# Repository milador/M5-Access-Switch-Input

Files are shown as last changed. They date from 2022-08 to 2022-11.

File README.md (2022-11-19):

# M5-Access-Switch-Input

A Bluetooth enabled Adaptive Switch Interface based on ESP32 M5StickC/M5StickCPlus, and the Switch Input module which offers up to two 3.5mm switch inputs. 

The Adaptive Switch Interface includes 4 operating modes: 

    1. Switch Mode
    2. Switch Mac Mode  
    3. Morse Keyboard Mode 
    4. Media Control Mode
    5. Settings Mode
	
The mode can be changed by pressing and holding Switch A for 4 seconds or pressing M5 button.

<p align="center">
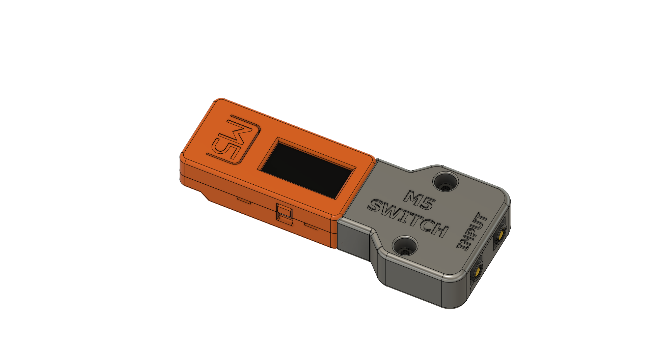
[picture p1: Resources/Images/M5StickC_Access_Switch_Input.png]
M5StickC_Access_Switch_Input

</p>

## Requirements and setup instructions 
The setup process is divided to three main catagories:

  1. [Hardware](./Hardware/) : The required hardware and design files
  2. [Software](./Software/) : The required software
  3. [Documentation](./Documentation/) : The assembly guide,user guide and other documents 

## License

### MIT License

Copyright (c) 2022 milador

Permission is hereby granted, free of charge, to any person obtaining a copy of this software and associated documentation files (the "Software"), to deal in the Software without restriction, including without limitation the rights to use, copy, modify, merge, publish, distribute, sublicense, and/or sell copies of the Software, and to permit persons to whom the Software is furnished to do so, subject to the following conditions:

The above copyright notice and this permission notice shall be included in all copies or substantial portions of the Software.

THE SOFTWARE IS PROVIDED "AS IS", WITHOUT WARRANTY OF ANY KIND, EXPRESS OR IMPLIED, INCLUDING BUT NOT LIMITED TO THE WARRANTIES OF MERCHANTABILITY, FITNESS FOR A PARTICULAR PURPOSE AND NONINFRINGEMENT. IN NO EVENT SHALL THE AUTHORS OR COPYRIGHT HOLDERS BE LIABLE FOR ANY CLAIM, DAMAGES OR OTHER LIABILITY, WHETHER IN AN ACTION OF CONTRACT, TORT OR OTHERWISE, ARISING FROM, OUT OF OR IN CONNECTION WITH THE SOFTWARE OR THE USE OR OTHER DEALINGS IN THE SOFTWARE.

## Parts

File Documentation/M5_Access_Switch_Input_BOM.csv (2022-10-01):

Index | Quantity | Component | Digikey Part Number | Manufacturer Part Number | Description | Unit Price (CAD) | Price (CAD) | Link
1 | 1 |  | 2221-K016-P-ND | K016-P | M5STICKC PLUS ESP32-PICO IOT KIT | 31.48 | 31.48 | https://www.digikey.ca/en/products/detail/m5stack-technology-co-ltd/K016-P/13148797
2 | 2 | SW1,SW2 | CP-43514-ND | SJ-43514 | CONN JACK 4COND 3.5MM | 1.48 | 2.96 | https://www.digikey.ca/en/products/detail/SJ-43514/CP-43514-ND/368146
3 | 2 | OK1,OK2 | 160-1366-5-ND | LTV-817 | OPTOISOLATR 5KV TRANSISTOR 4-DIP | 0.58 | 1.16 | https://www.digikey.ca/en/products/detail/liteon/LTV-817/385836
4 | 1 | JP1 | 609-3321-ND | 68016-208HLF | CONN HEADER R/A 8POS 2.54MM | 0.7 | 0.7 | https://www.digikey.ca/en/products/detail/amphenol-cs-fci/68016-208HLF/1878499
5 | 2 | R1,R2 | S1KQCT-ND | CFM14JT1K00 | RES 1K OHM 5% 1/4W AXIAL | 0.15 | 0.3 | https://www.digikey.ca/en/products/detail/stackpole-electronics-inc/CFM14JT1K00/1742111
6 | 2 | R3,R4 | 738-CFM14JA470RCT-ND | CFM14JA470R | RES 470 OHM 5% 1/4W AXIAL | 0.15 | 0.3 | https://www.digikey.ca/en/products/detail/stackpole-electronics-inc/CFM14JA470R/1742225
7 | 2 | N/A | 145-50M025045P006-ND | 50M025045P006 | PAN PHILLIPS SCREW, M2.5 X 4.5 T | 0.23 | 0.46 | https://www.digikey.ca/en/products/detail/essentra-components/50M025045P006/11638590
8 | 2 | N/A | 36-9600-ND | 9600 | HEX NUT 1/4" STEEL 4-40 | 0.16 | 0.32 | https://www.digikey.ca/en/products/detail/keystone-electronics/9600/2746248
 |  |  |  |  |  | Total Price (CAD) | 37.68

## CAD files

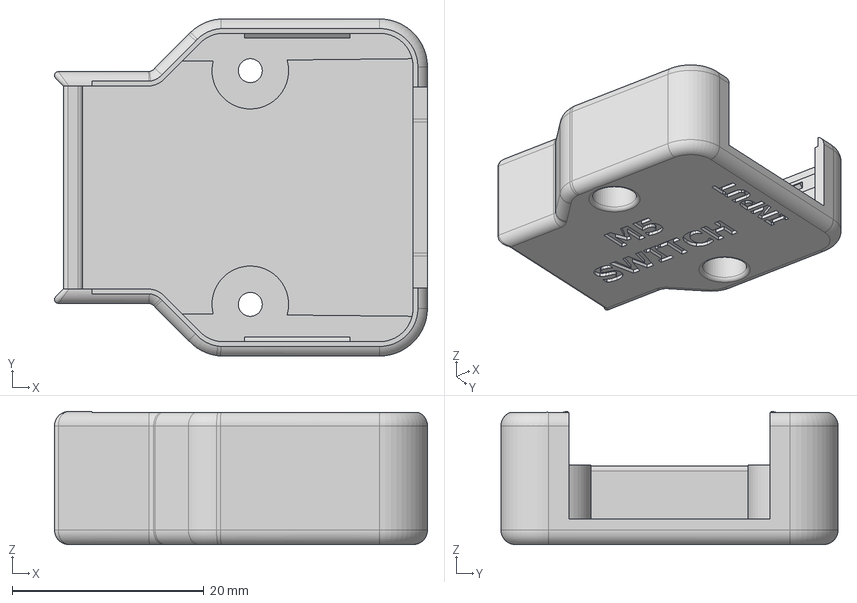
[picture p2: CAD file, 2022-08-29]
Hardware/Case/STEP/M5StickC_Switch_Input_Main.step
38.9 x 35.2 x 13.9 mm

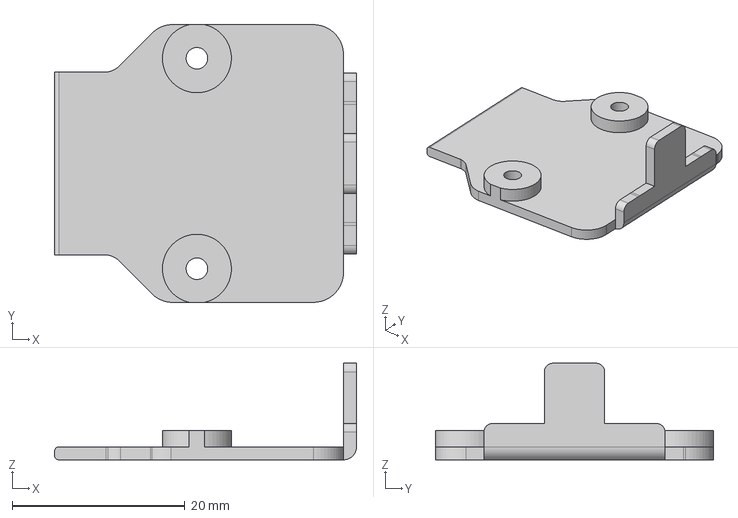
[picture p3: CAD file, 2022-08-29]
Hardware/Case/STEP/M5StickC_Switch_Input_Bottom.step
35.0 x 32.2 x 11.2 mm

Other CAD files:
Hardware/Case/STL/M5StickC_Switch_Input_Bottom.stl
Hardware/Case/STL/M5StickC_Switch_Input_Main.stl

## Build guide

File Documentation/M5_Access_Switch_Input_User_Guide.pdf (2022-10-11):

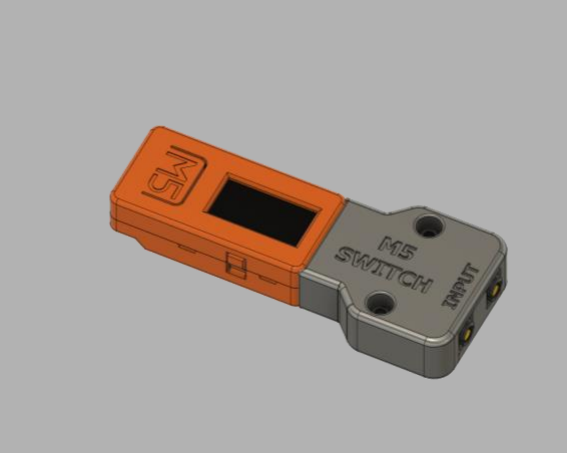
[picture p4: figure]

# M5 ACCESS SWITCH INPUT USER GUIDE (V1.0)

A wireless switch interface device

Milad Hajihassan
https://github.com/milador/M5-Access-Switch-Input

1

## Contents

Usage requirements | 2
Usage Components | 2
Usage Process | 2
How to Use? | 2
How to Customize? | 2
Sleep Mode | 3

2

## Usage requirements

Usage Components

1. Adaptive Switch x 2 ( Example: AJelly Bean (https://www.ablenetinc.com/jelly-bean) )

## Usage Process

How to Use?

1. Connect two Adaptive Switches to the Switch Input module through 3.5mm switch connectors.
1.1. Switch A
1.2. Switch B
2. Connect and pair to the host device (Example: Windows 10 PC)

On Windows 10:

2.1. Select Start > Settings > Devices > Bluetooth & other devices 2.2. Select Add Bluetooth or other device > Bluetooth. 2.3. Choose Qwiic BLE Switch and follow additional instructions if they appear. 2.4. Select Done once the device is paired.
3. Switch between modes by press and holding Switch A for 4 seconds or by pressing M5 button.
3.1. Switch Mode: Windows and Android, Switch A : a Key, Switch B : b Key
3.2. Switch Mac Mode: Mac, Switch A : F1 Key, Switch B : F2 Key
3.3. Morse Keyboard Mode: Switch A : Dot, Switch B : Dash
3.4. Media Control Mode: Switch A : Previous Track, Switch B : Next Track
3.5. Settings Mode: Change reaction time, Switch A : Decrease Reaction level, Switch B : Increase Reaction level

How to Customize?

1. Enter Settings Mode by press holding switch A 3 times for 4 seconds or by pressing M5

button. The screen will display a text in yellow to indicate it's in Settings Mode.

3

2. Press Switch A to Decrease Reaction level ( Maximum is 1 ) : 500ms
3. Press Switch B to Increase Reaction level ( Minimum is 10 ) : 50ms

Sleep Mode

The device goes to sleep mode if it’s not used for more than one minute and automatically wakes up every 3 minutes. The device can be woken up if switch A or Switch B is pressed when the device is in sleep mode.

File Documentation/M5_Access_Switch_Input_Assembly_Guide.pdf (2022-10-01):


# M5 ACCESS SWITCH INPUT ASSEMBLY GUIDE (V1.0)

A wireless switch interface device

### Milad Hajihassan

https://github.com/milador/M5-Access-Switch-Input

1

## Contents

Components List | 2
Software | 3
Installing Arduino IDE | 3
Installing Arduino Libraries | 3
Board Support Packages | 3
Required Software and libraries | 3
Uploading Software | 5
Hardware Assembly | 6
Enclosure design | 6
M5 Access Switch Input Assembly | 7

2

## Components List

1. M5STICKC PLUS ESP32-PICO IOT KIT x 1
2. SJ-43514 3.5MM TRRS AUDIO JACK x 2
3. LTV-817 OPTOISOLATR x 2
4. 8 POSITION MALE RIGHT ANGLE HEADER x 1
5. 1K OHM 1/4W RESISTOR x 2
6. 470 OHM 1/4W RESISTOR x 2
7. M2.5 SCREW (8MM) x 2
8. M2.5 SCREW NUT x 2

The bill of materials can also be downloaded from GitHub repository under main directory.

https://github.com/milador/M5-Access-Switch-

Input/blob/main/Documentation/M5_Access_Switch_Input_BOM.csv (https://github.com/milador/M5-Access-Switch-Input/blob/main/Documentation/M5_Access_Switch_Input_BOM.csv)

3

## Software

The Switch Input software can be downloaded from the GitHub repository under software directory.

https://raw.githubusercontent.com/milador/M5-Access-Switch-Input/develop/Software/M5_Access_Switch_Input_Software/M5_Access_Switch_Input_Software.ino (https://raw.githubusercontent.com/milador/M5-Access-Switch-Input/main/Software/M5_Access_Switch_Input_Software/M5_Access_Switch_Input_Software.ino)

### Installing Arduino IDE

The Arduino IDE is required to compile and upload the source code to the MCU in your M5StickC device. You can download and install the Arduino from official Arduino website that you can find using following link:

https://www.arduino.cc/en/software

### Installing Arduino Libraries

The following instructions on how to install additional Arduino libraries helps you to get started with setting up Arduino IDE with required libraries and dependencies.

https://www.arduino.cc/en/guide/libraries

Board Support Packages
You can find the official instructions to install Board Support Packages on M5Stack website using following link:

https://docs.m5stack.com/en/quick_start/m5stickc/arduino

Alternatively, you can perform following instructions to install Board Support Packages:

1. Open and start the Arduino IDE.
2. Go to File > Preferences.
3. Add following link as a new line under Additional Board Manager URLs
- https://m5stack.oss-cnshenzhen.aliyuncs.com/resource/arduino/package_m5stack_index.json (https://m5stack.oss-cn-shenzhen.aliyuncs.com/resource/arduino/package_m5stack_index.json)
4. Restart the Arduino IDE
5. Open the Boards Manager option from the Tools > Board menu and install M5Stack by M5Stack official
6. Wait until the IDE finishes installing the cross-compiling toolchain and tools associated with Board Support Package. This may take few minutes.
7. That’s it! The installation of Board Support Packages is finished.

Required Software and libraries
The software requirements:
- M5_Access_Switch_Input_Software.ino (https://raw.githubusercontent.com/milador/M5-Access-Switch-Input/develop/Software/M5_Access_Switch_Input_Software/M5_Access_Switch_Input_Software.ino)
- M5StickC Plus (https://github.com/m5stack/M5StickC-Plus)
- ESP32-BLE-Keyboard (https://github.com/milador/ESP32-BLE-Keyboard)
- StopWatch Library (https://github.com/RobTillaart/Stopwatch_RT)
- EasyMorse Library (https://github.com/milador/EasyMorse)

4

Note: This project is using edited version of ESP32-BLE-Keyboard library by T-vK.

You can use the following instructions to download and install the required libraries:

1) Visit the M5StickC-Plus library github repository page.
2) Click on Code > Download Zip to download M5StickC-Plus.
3) Extract M5StickC-Plus-master.zip file
4) Rename M5StickC-Plus-master folder to M5StickC-Plus folder under M5StickC-Plus-master subdirectory.
5) Copy or move M5StickC-Plus folder to Arduino installation library subdirectory. As an example: This is found under C:\Program Files (x86)\Arduino\libraries in windows 10.
6) Visit the ESP32-BLE-Keyboard library github repository page.
7) Click on Code > Download Zip to download ESP32-BLE-Keyboard.
8) Extract ESP32-BLE-Keyboard-master.zip file
9) Rename ESP32-BLE-Keyboard-master folder to ESP32-BLE-Keyboard folder under ESP32-BLE-Keyboard-master subdirectory.
10) Copy or move ESP32-BLE-Keyboard folder to Arduino installation library subdirectory. As an example: This is found under C:\Program Files (x86)\Arduino\libraries in windows 10.
11) Visit the StopWatch library github repository page.
12) Click on Code > Download Zip to download StopWatch library.
13) Extract Stopwatch_RT-master.zip file
14) Rename Stopwatch_RT-master folder to Stopwatch folder under Stopwatch_RT-master subdirectory.
15) Copy or move Stopwatch folder to Arduino installation library subdirectory. As an example: This is found under C:\Program Files (x86)\Arduino\libraries in windows 10.
16) Visit the EasyMorse library github repository page.
17) Click on Code > Download Zip to download EasyMorse library.
18) Extract EasyMorse-master.zip file
19) Rename EasyMorse-master folder to EasyMorse folder under EasyMorse-master subdirectory.
20) Copy or move EasyMorse folder to Arduino installation library subdirectory. As an example: This is found under C:\Program Files (x86)\Arduino\libraries in windows 10.
21) Visit the M5_Access_Switch_Input_Software.ino raw source code file under Software directory.
22) Right click on the source code or any place on this page and select Save Page As…
23) Select the directory you would like to save the software in your computer.
24) Change File name from M5_Access_Switch_Input_Software to M5_Access_Switch_Input_Software.ino
25) Change Save as type to All Files.
26) Click on Save button.
27) Open the directory you selected in step 23.
28) Double left click or open M5_Access_Switch_Input_Software file
29) Arduino IDE will ask your permission to create a new sketch folder named M5_Access_Switch_Input_Software and move M5_Access_Switch_Input_Software.ino under this folder.
30) Click on the Ok button.
31) Arduino IDE should now open the M5_Access_Switch_Input_Software.ino file automatically.

5

Uploading Software
Note: Make sure all files are included in your local copy of Software directory before uploading it to the M5StickC device. The libraries can be installed in Arduino libraries.

You can go ahead and upload the downloaded M5_Access_Switch_Input_Software.ino code to M5StickC using Arduino IDE once all the necessary libraries are installed.

1. Start the Arduino IDE
2. Open M5_Access_Switch_Input_Software.ino
3. Select the Board under Tools > Board > M5Stick Arduino Boards as M5Stick-C-Plus
4. Select the correct port number under Tools > Port which should show COM XX (M5Stick-C-Plus)

Note: It’s very important to make sure the correct Board and port number are selected as selecting the wrong board may result problems with bootloader of M5StickC device.

5. Press the Verify button to make sure there is no problem with the software and libraries.
6. Press Upload button

You can now go ahead and upload the software. Arduino IDE will show you a Done Uploading message indicating the software is uploaded to your M5StickC device.

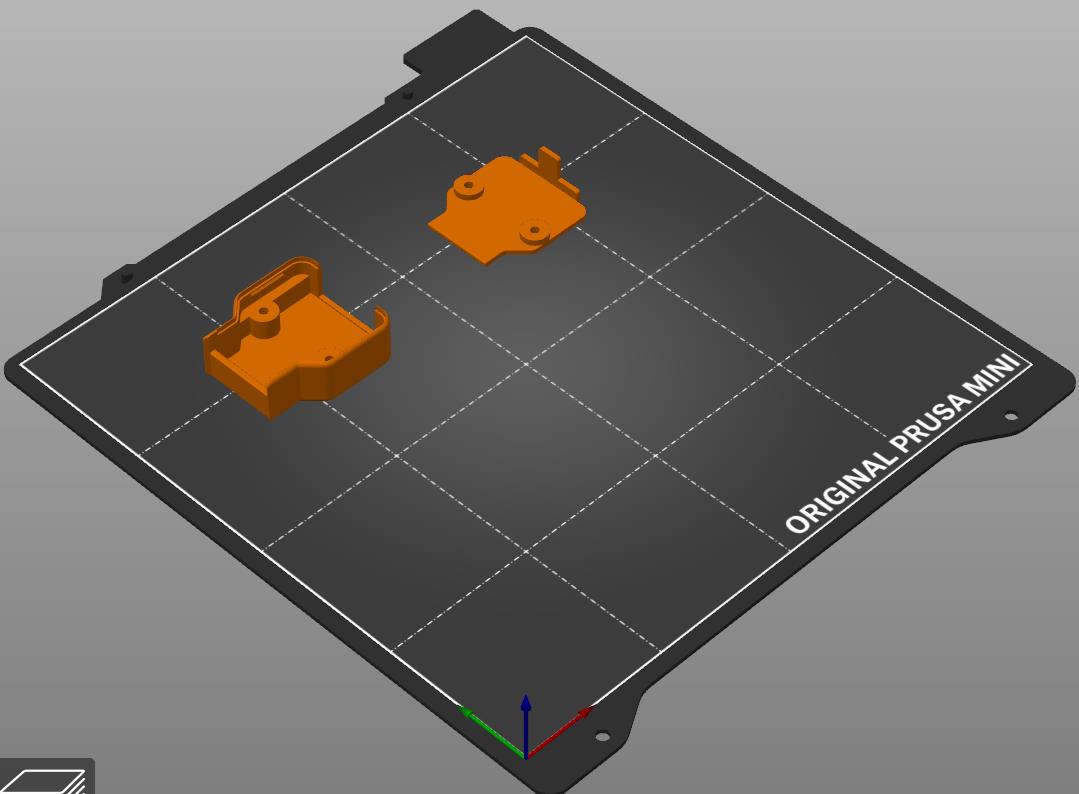
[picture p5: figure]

6

## Hardware Assembly

### Enclosure design

The enclosure/housing files in STL format can be downloaded from GitHub repository under Hardware and Case subdirectory.

- M5StickC_Switch_Input_Main.STL
- M5StickC_Switch_Input_Bottom.STL

https://github.com/milador/M5-Access-Switch-Input/tree/main/Hardware/Case/STL

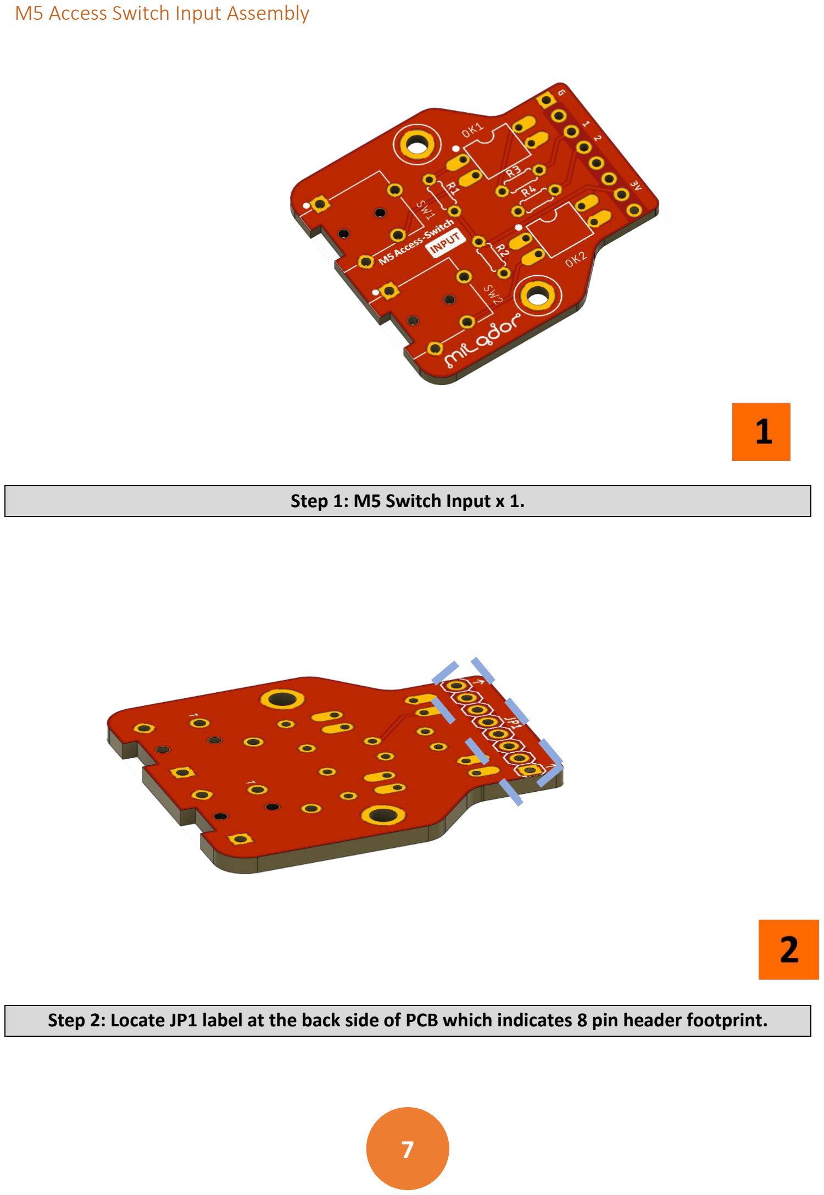
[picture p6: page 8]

7

### M5 Access Switch Input Assembly

Step 1: M5 Switch Input x 1.
Step 2: Locate JP1 label at the back side of PCB which indicates 8 pin header footprint.

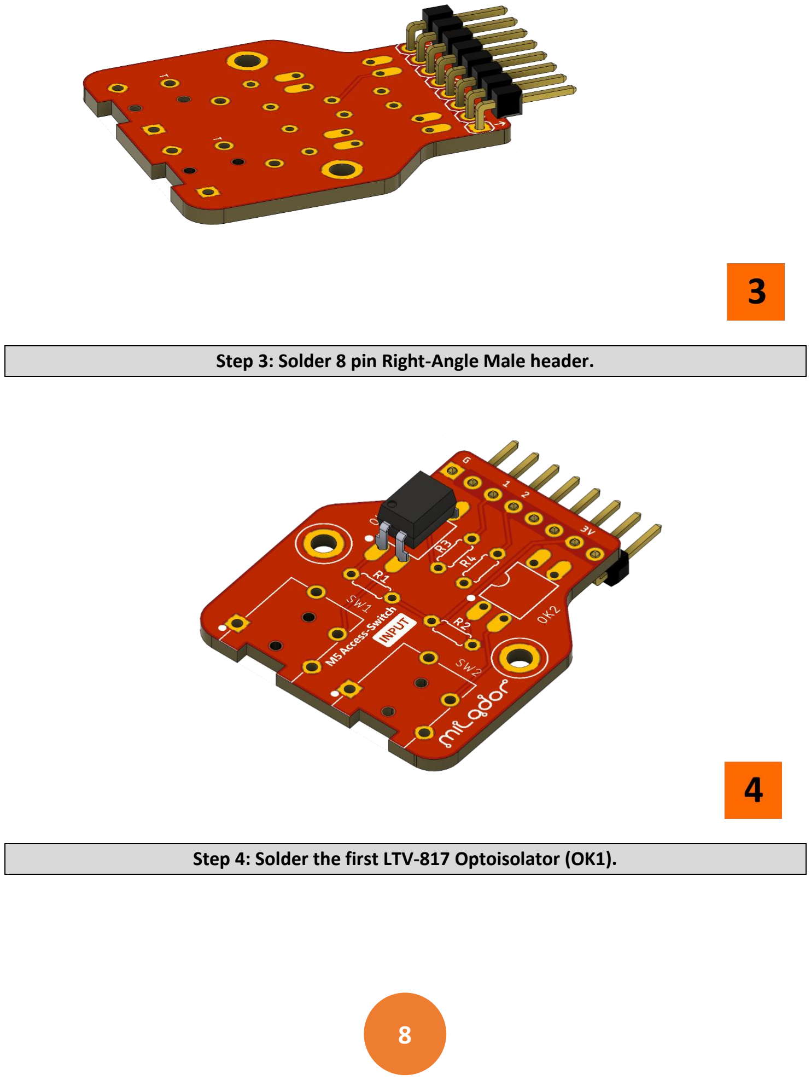
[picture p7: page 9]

8

Step 3: Solder 8 pin Right-Angle Male header.
Step 4: Solder the first LTV-817 Optoisolator (OK1).

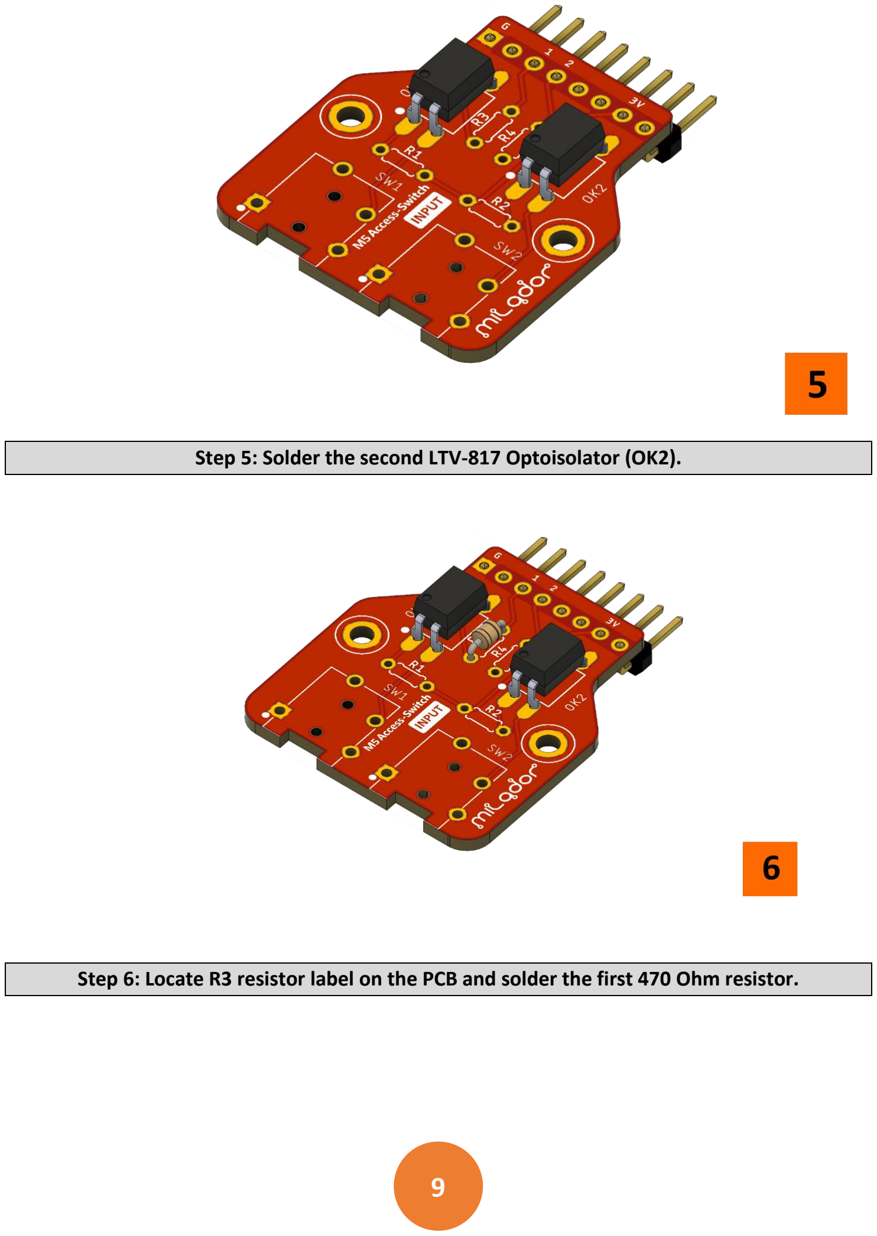
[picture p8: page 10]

9

Step 5: Solder the second LTV-817 Optoisolator (OK2).
Step 6: Locate R3 resistor label on the PCB and solder the first 470 Ohm resistor.

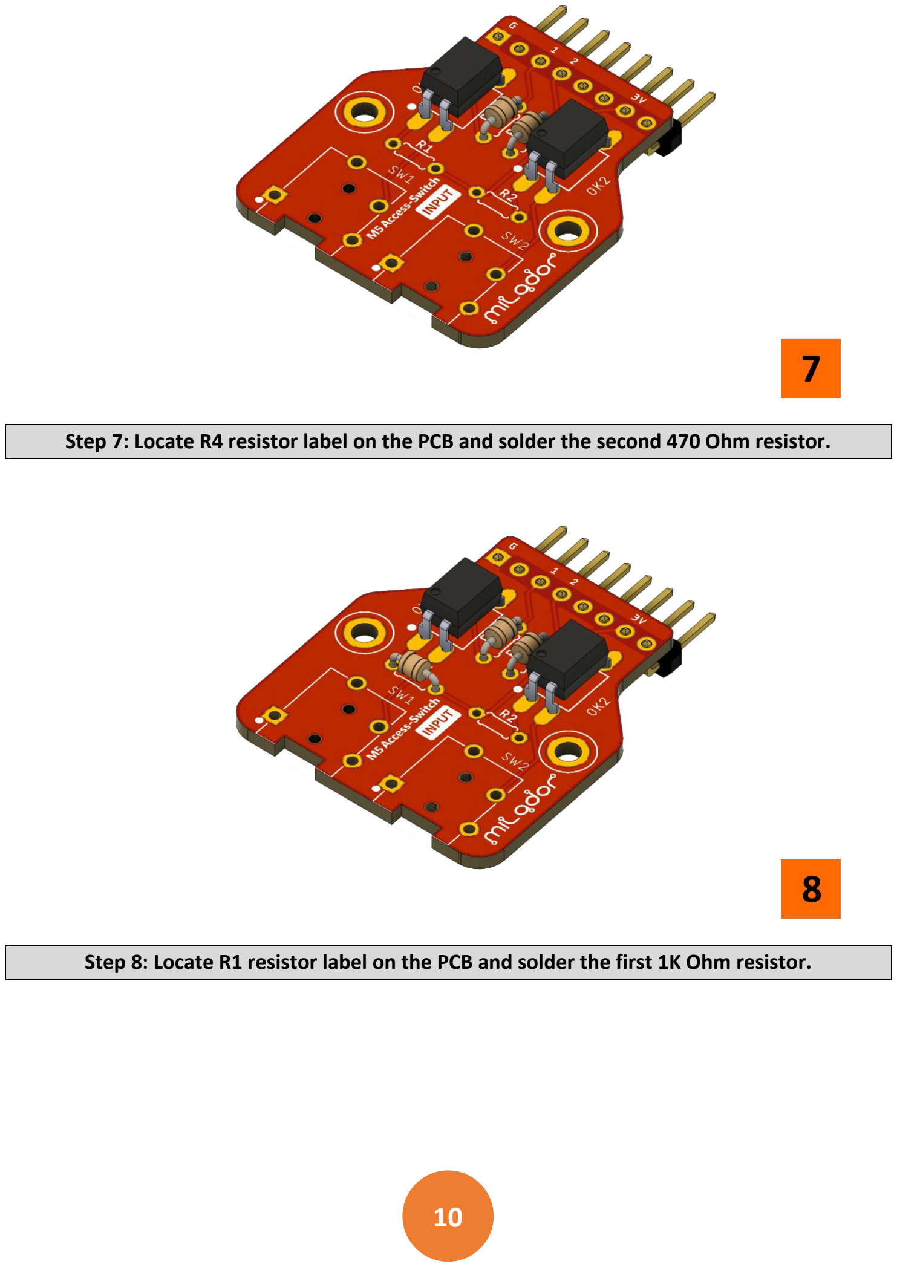
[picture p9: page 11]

10

Step 7: Locate R4 resistor label on the PCB and solder the second 470 Ohm resistor.
Step 8: Locate R1 resistor label on the PCB and solder the first 1K Ohm resistor.

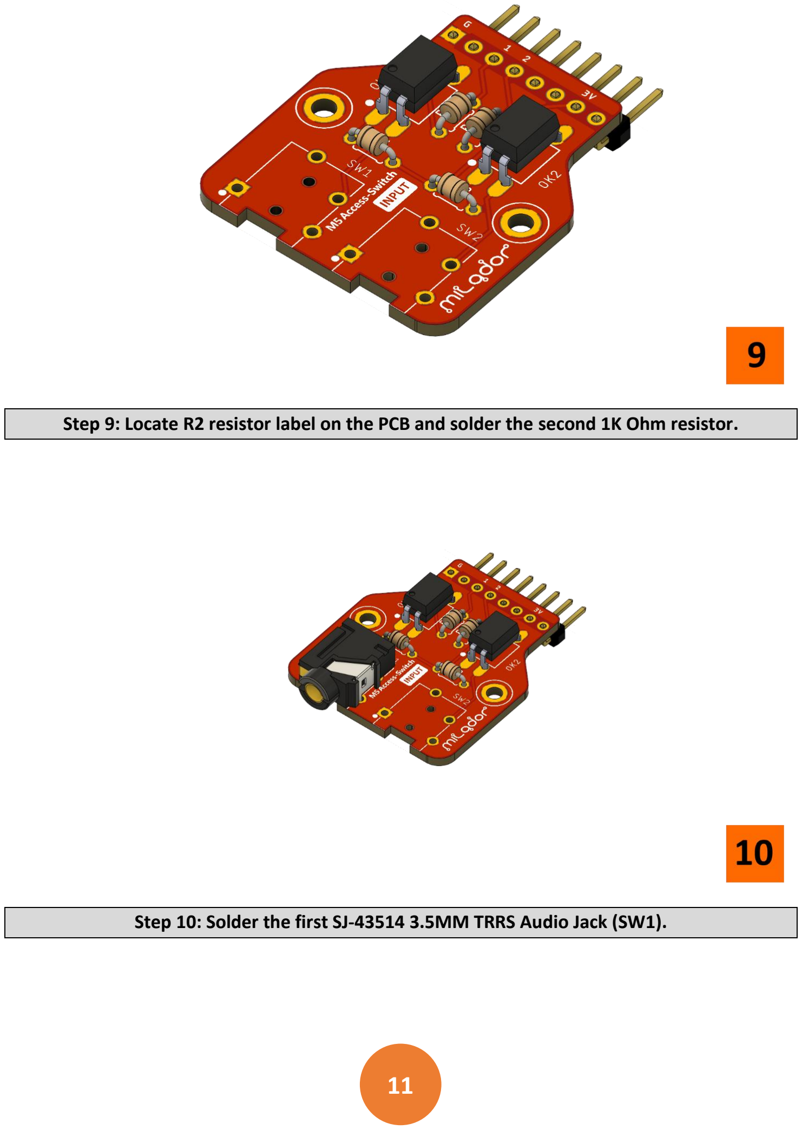
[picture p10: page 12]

11

Step 9: Locate R2 resistor label on the PCB and solder the second 1K Ohm resistor.
Step 10: Solder the first SJ-43514 3.5MM TRRS Audio Jack (SW1).

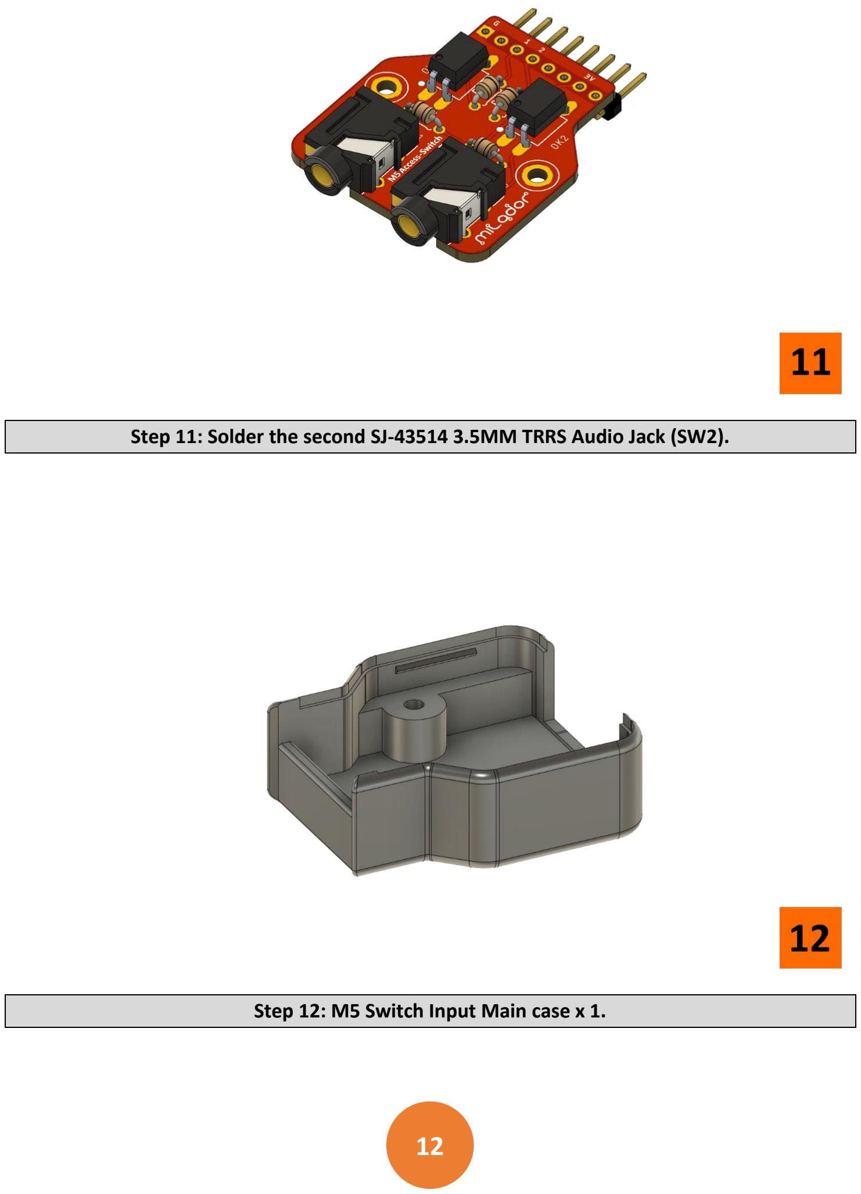
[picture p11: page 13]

12

Step 11: Solder the second SJ-43514 3.5MM TRRS Audio Jack (SW2).
Step 12: M5 Switch Input Main case x 1.

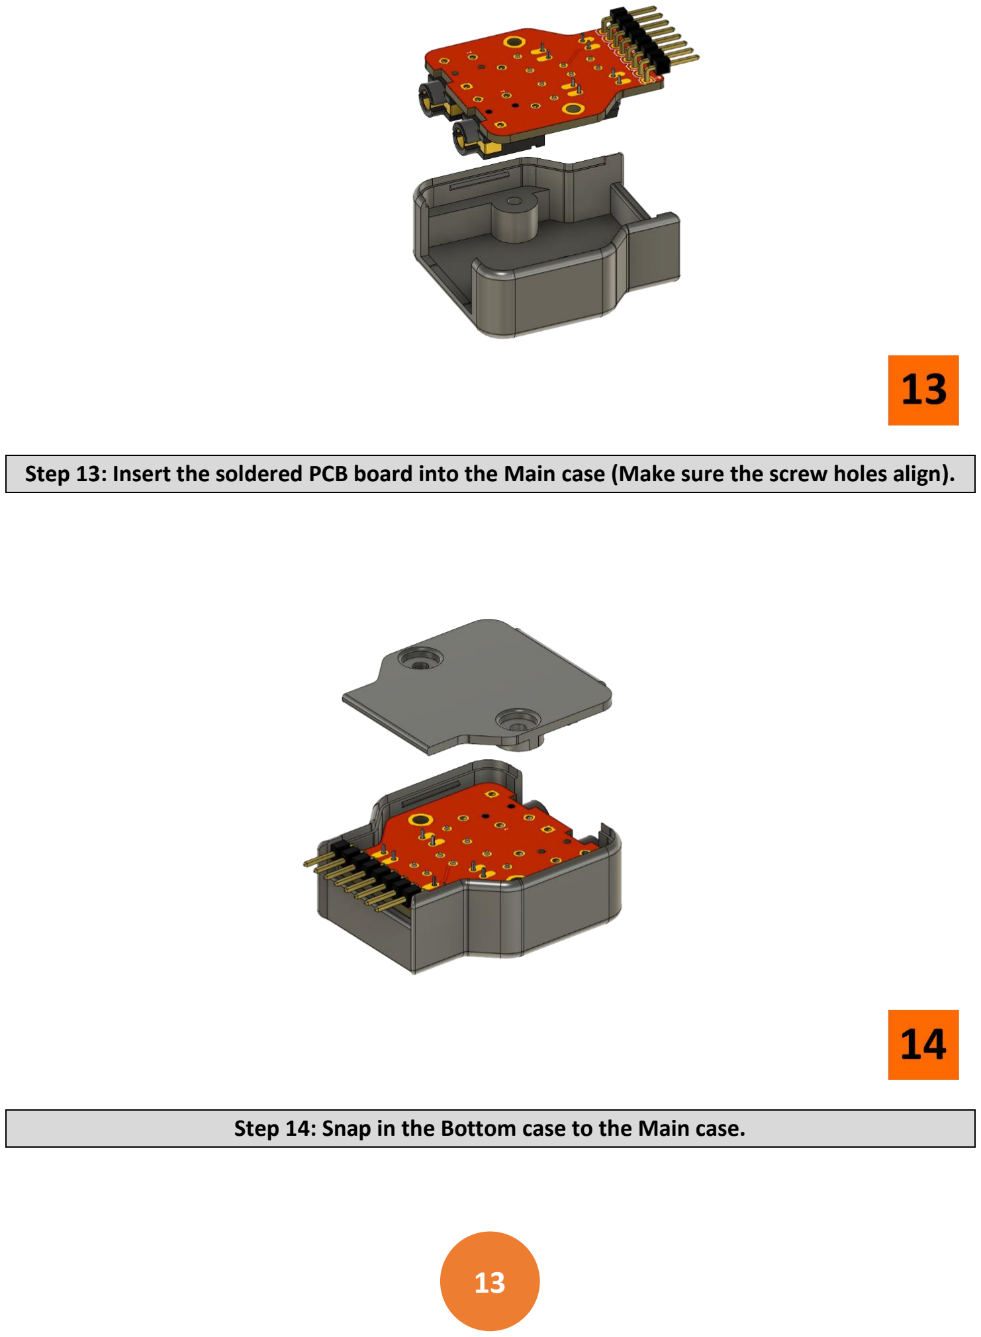
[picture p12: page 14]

13

Step 13: Insert the soldered PCB board into the Main case (Make sure the screw holes align).
Step 14: Snap in the Bottom case to the Main case.

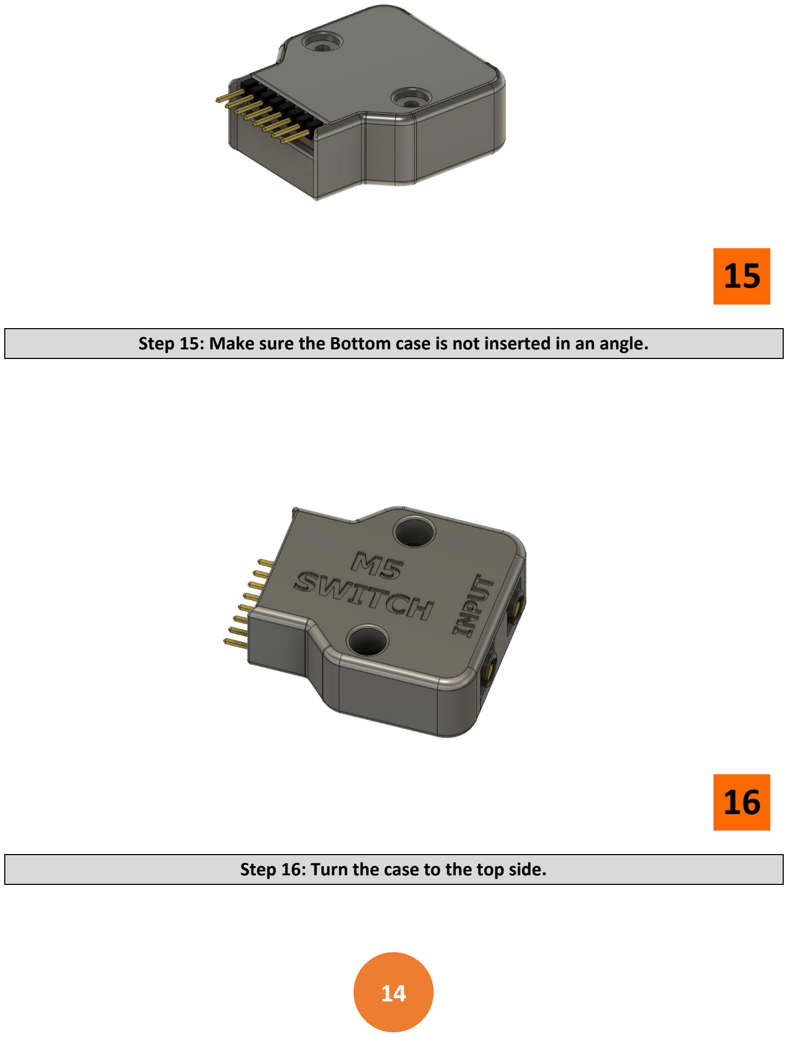
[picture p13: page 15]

14

Step 15: Make sure the Bottom case is not inserted in an angle.
Step 16: Turn the case to the top side.

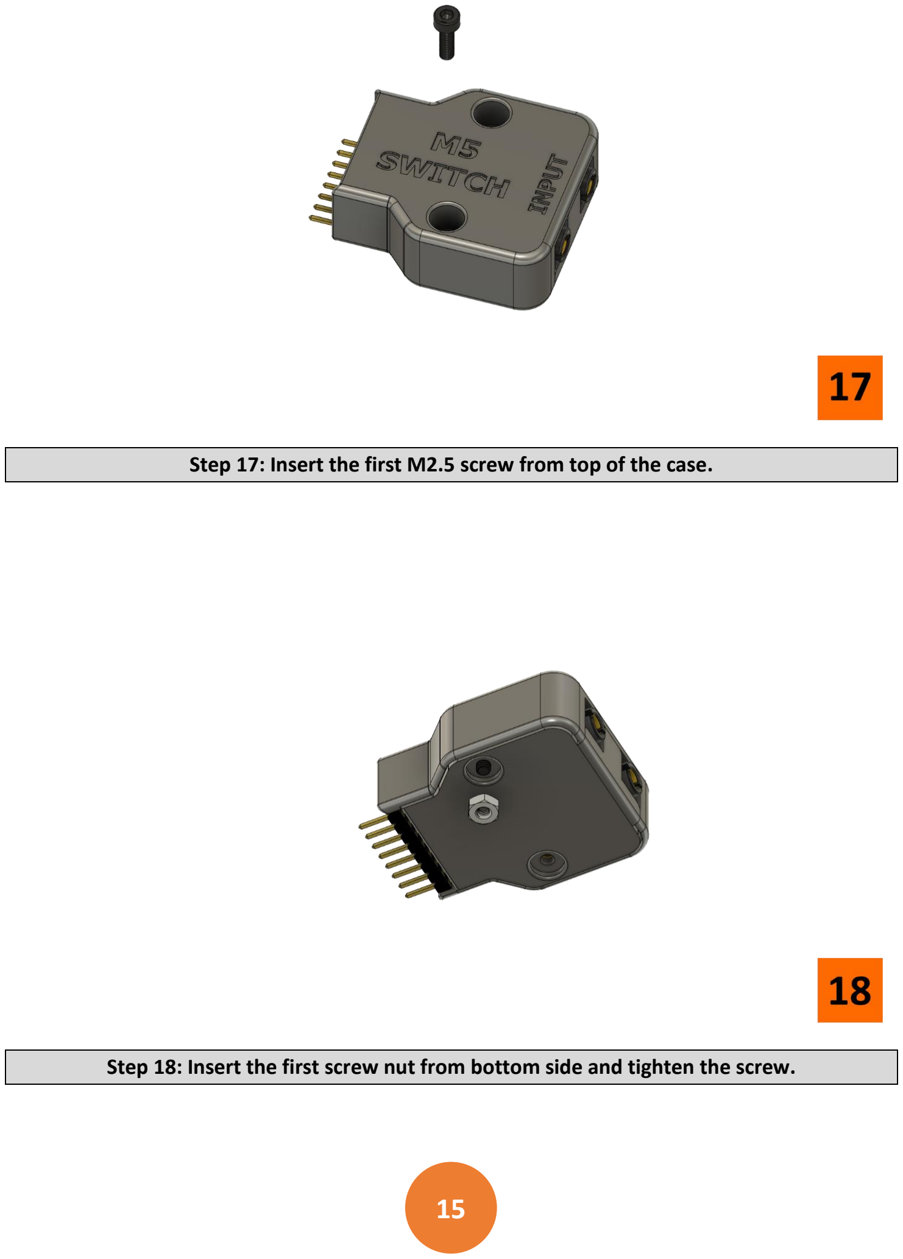
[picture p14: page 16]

15

Step 17: Insert the first M2.5 screw from top of the case.
Step 18: Insert the first screw nut from bottom side and tighten the screw.

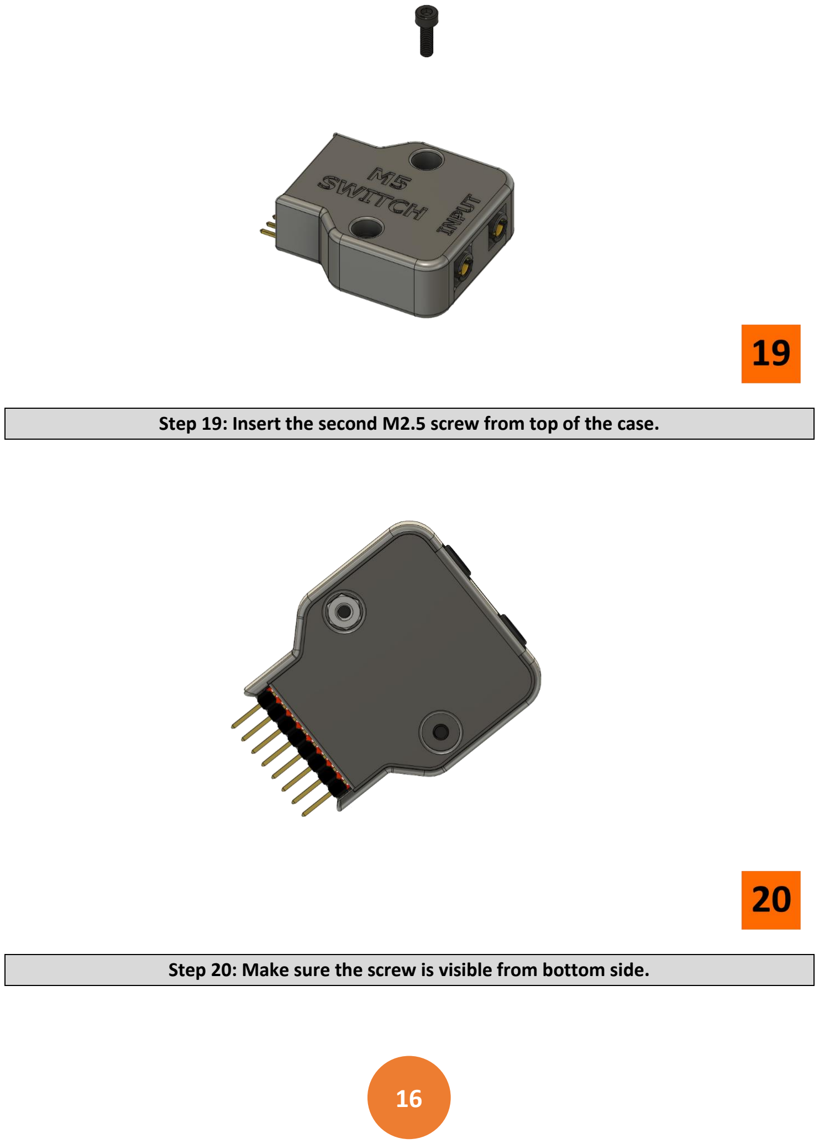
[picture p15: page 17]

16

Step 19: Insert the second M2.5 screw from top of the case.
Step 20: Make sure the screw is visible from bottom side.

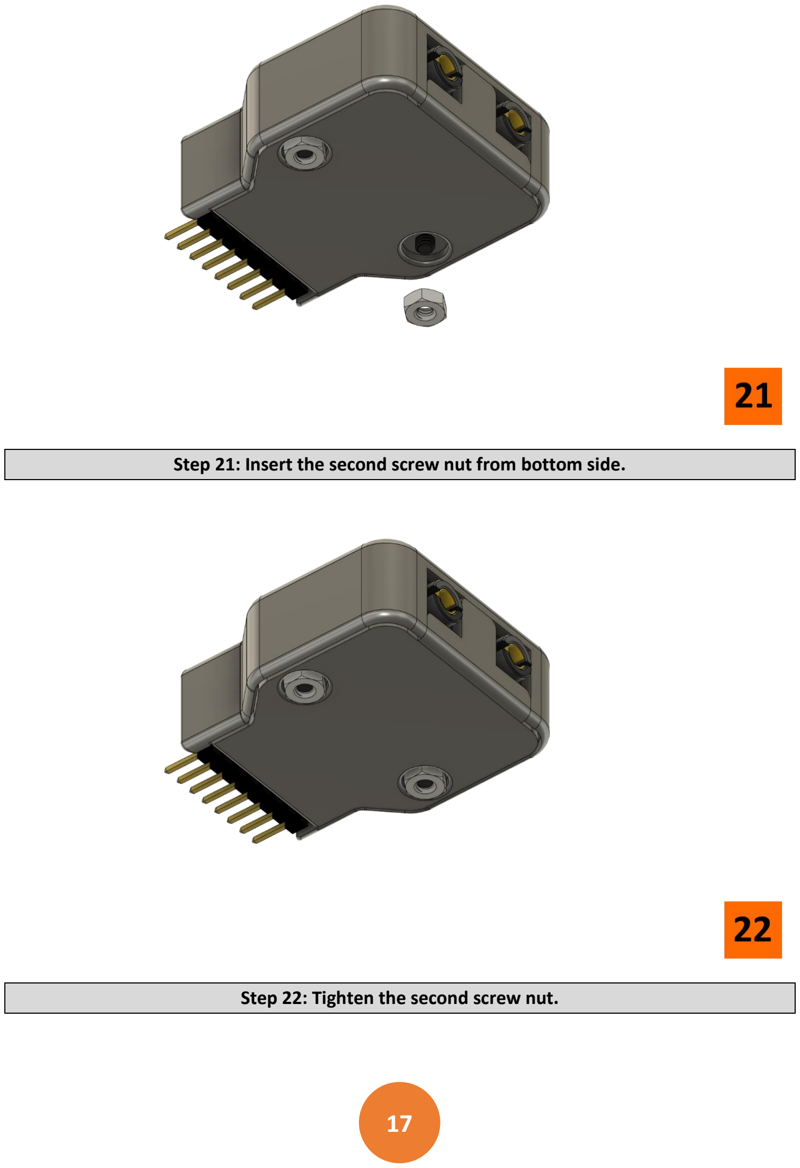
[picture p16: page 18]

17

Step 21: Insert the second screw nut from bottom side.
Step 22: Tighten the second screw nut.

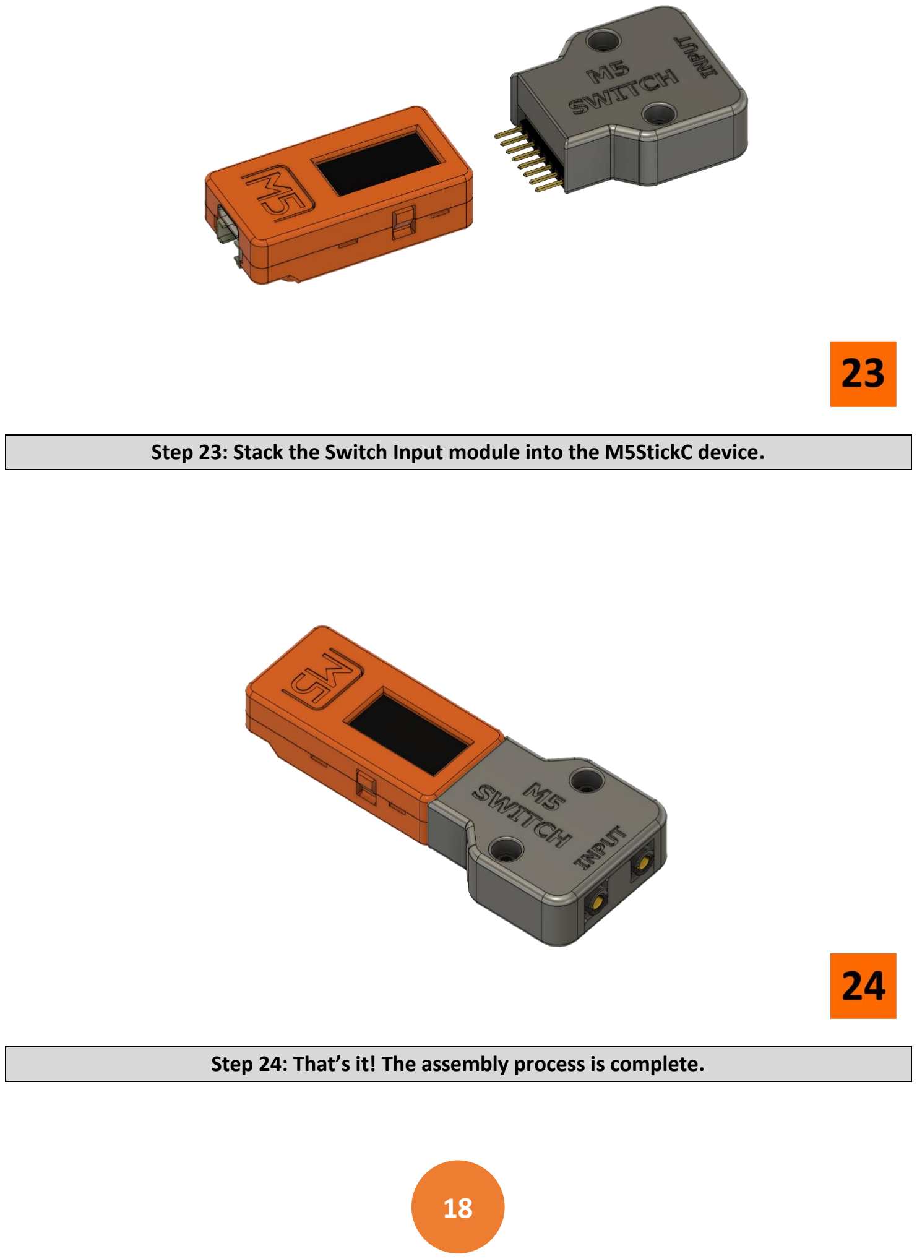
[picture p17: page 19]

18

Step 23: Stack the Switch Input module into the M5StickC device.
Step 24: That’s it! The assembly process is complete.

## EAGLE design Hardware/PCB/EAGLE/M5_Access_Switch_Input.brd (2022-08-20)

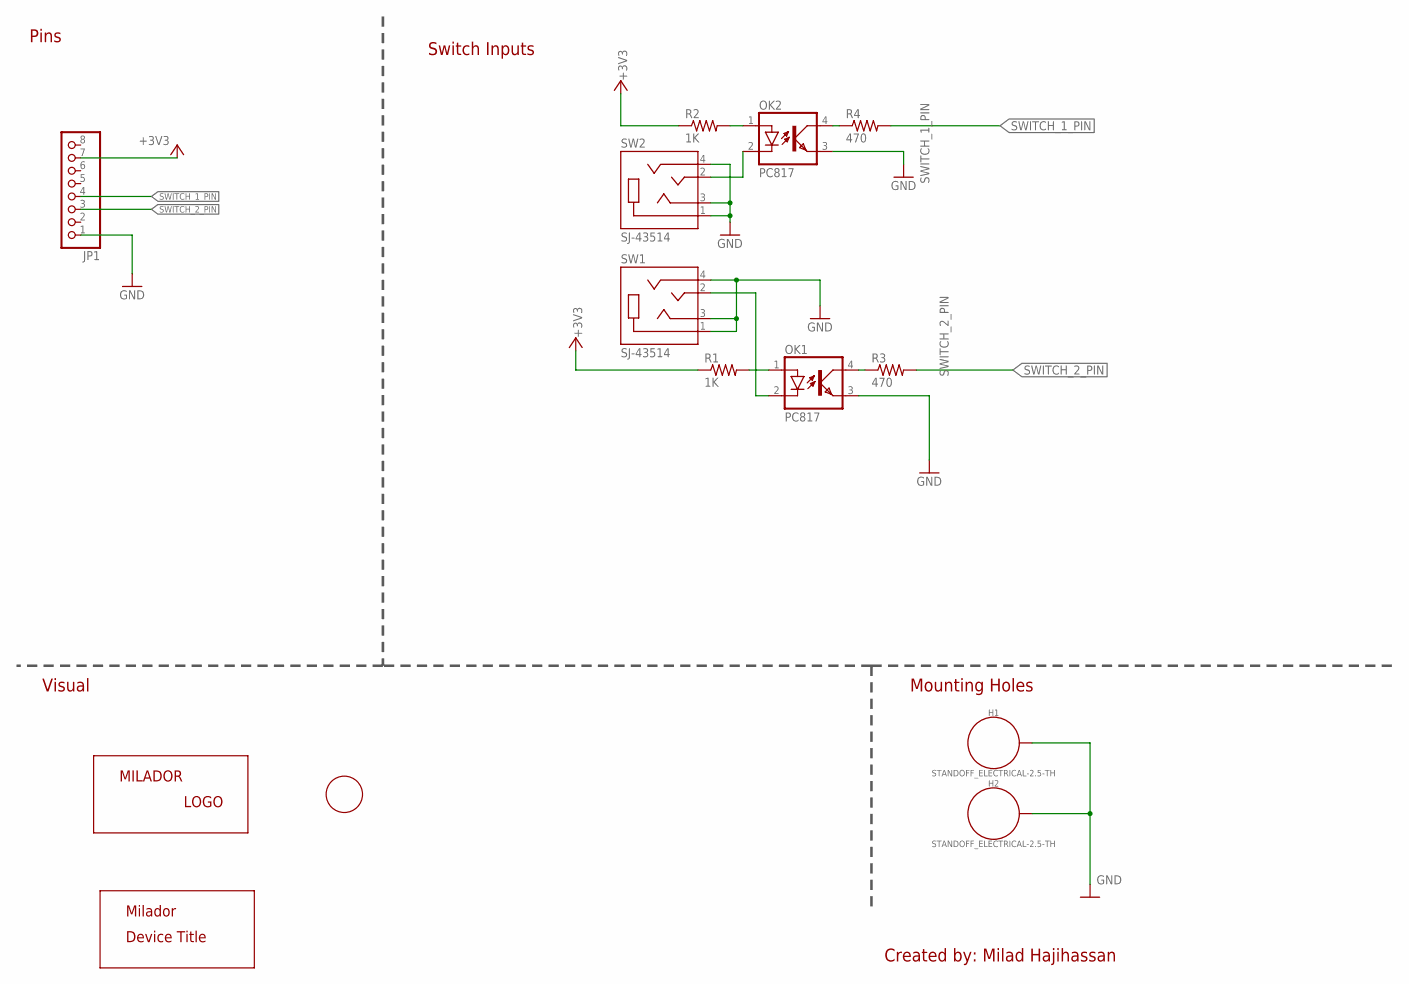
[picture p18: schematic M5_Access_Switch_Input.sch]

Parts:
H1, H2: STANDOFF_ELECTRICAL-2.5-TH; STANDOFF-ELECTRICAL-2.5-TH
JP1: HEADER_MALE-1X8ROUND-RA; 1X08_ROUND_RA
LABEL_DEVICE_TOP: MILADOR-DEVICE-M5-ACCESS-SWITCH; MILADOR_M5_ACCESS_SWITCH
LABEL_INPUT_TOP: MILADOR-SWITCH-NAME-SW-INPUT; SWITCH-INPUT
LABEL_LOGO_TOP: MILADOR-LOGO-SM; MILADOR_LOGO2
OK1, OK2: PC817; DIL04
R1, R2: 1K; RESISTOR_0204/5
R3, R4: 470; RESISTOR_0204/5
SW1, SW2: SJ-43514; CUI_SJ-43514

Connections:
+3V3: JP1.7, R1.1, R2.1
GND: H1.P1, H2.P1, JP1.1, OK1.3 (EMIT), OK2.3 (EMIT), SW1.1 (SLEEVE), SW1.3 (RING1), SW1.4 (RING2), SW2.1 (SLEEVE), SW2.3 (RING1), SW2.4 (RING2)
unnamed: OK1.1 (A), R1.2
unnamed: OK1.4 (COL), R3.1
unnamed: OK1.2 (C), SW1.2 (TIP)
unnamed: OK2.1 (A), R2.2
unnamed: OK2.4 (COL), R4.1
unnamed: OK2.2 (C), SW2.2 (TIP)
SWITCH_1_PIN: JP1.4, R4.2
SWITCH_2_PIN: JP1.3, R3.2

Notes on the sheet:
Switch Inputs
Pins
Mounting Holes
Visual
Created by: Milad Hajihassan

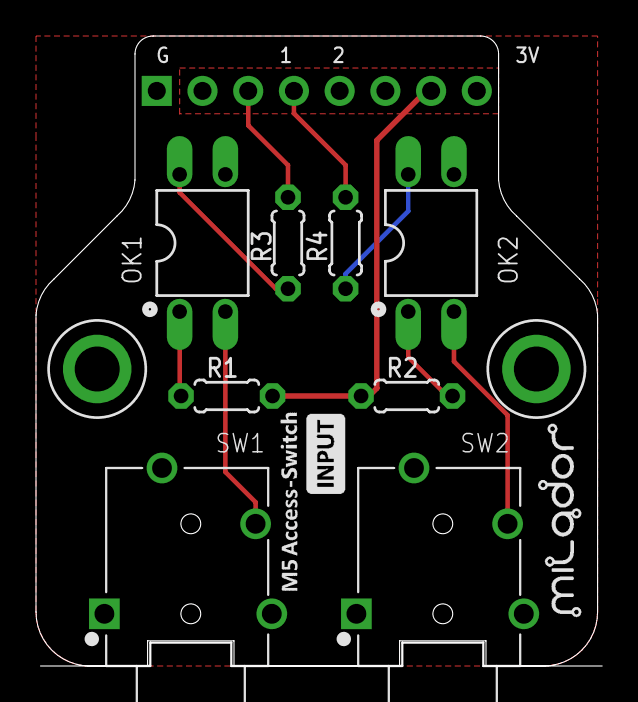
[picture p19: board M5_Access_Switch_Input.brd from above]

Board: 2 copper layers, 31.2 x 35.0 mm, 14 parts (1 on the bottom side), 10 nets.

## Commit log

2022-08-20 Added Stereo jack design
    [M5StickC_Access_Switch_Input.brd, M5StickC_Access_Switch_Input.sch]
2022-08-20 Changed the design to dual mono jacks
    [M5_Access_Switch_Dual_Input.brd, M5_Access_Switch_Dual_Input.sch]
2022-08-20 Renamed Design files
    [M5_Access_Switch_Input.brd, M5_Access_Switch_Input.sch]
2022-08-29 Added enclosure/case files
    [M5StickC_Switch_Input_Bottom.step, M5StickC_Switch_Input_Bottom.stl, M5StickC_Switch_Input_Main.step, M5StickC_Switch_Input_Main.stl]
2022-08-29 Added BOM
    [M5_Access_Switch_Input_BOM.xlsx]
2022-10-01 Updated part list
    [M5_Access_Switch_Input_BOM.csv, M5_Access_Switch_Input_BOM.xlsx]
2022-10-01 Added assembly guide
